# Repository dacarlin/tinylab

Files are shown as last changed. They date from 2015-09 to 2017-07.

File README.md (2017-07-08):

# TinyLab: Open Source Laboratory Robotics 

TinyLab is a collection of hardware design, protocols, and parts for building a modern biological laboratory using off-the-shelf parts and a 3D printer. Started as a [liquid handling kit for 3D printers](https://github.com/ryneches/tinylab), TinyLab is an open, collaborative project that seeks to provide researchers around the world the ability to create their own low cost, high quality tools for molecular biology, protein design, and organism design. 

## Contributing 

Contributions are welcome! This project is still in its early stages, and we welcome contributions at any level, from high-level approach advice to detailed plans and designs. Send us a pull request, or an email if we have help. Thanks! 

## Hardware 

### Block: Pipet Affector 

A open source design of a single-channel pipet affector module that can be built from off-the-shelf parts and 3D-printed designs provided here. 

#### Assembly 

1. 3D print the provided parts 
2. Purchase the items from the BOM 
3. Assemble according to instructions in `README.md` in `pipet` directory 

### Much4: Cartesian Frame Bot 

Open build from OpenBuilds.org ([Much4](http://www.openbuilds.com/threads/much4-a-printed-version-of-the-laser-v.547/)) showing a simple XY Cartesian bot that accepts our `pipet` design. 

### Jordan: Liquid Handler 

Second iteration (cantilever) liquid handling robot, nicknamed "Jordan". 

#### Assembly 

1. Print the parts in `parts/cantilever` and `parts/pipet`
1. Bolt the frame together 
1. Bolt on printed parts 
1. Install motors and electronics and test 
1. Run belts and pulleys 
1. Instal pipet assembly (see `pipet`) 

## Software 

### Autoprotocol-GCode Compiler 

Originally, this project was based on Transcriptic's [Autoprotocol language for specifying biological protocols](http://autoprotocol.org). However, since Transcriptic is no longer available for use, this may be of only historical interest. 

### WetTraffic: Liquid Handler Control 

Enables control of Jordan Liquid Handler using Python. 

### Trains: Scheduler 

Scheduler for handling the carriages that move plates between instruments in the work cell.

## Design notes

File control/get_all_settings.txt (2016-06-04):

{"1":n}    return motor 1 settings
{"2":n}
{"3":n}
{"4":n}
{"x":n}    return X axis settings
{"y":n}
{"z":n}
{"a":n}
{"b":n}
{"c":n}
{"sys":n}  return system settings
{"pos":n}  return work coordinate positions fox XYZABC axes. In mm or inches depending on G20/G21
{"mpo":n}  return absolute machine positions fox XYZABC axes. Always in mm, regardless of G20/G21
{"ofs":n}  return current offsets fox XYZABC axes. Sums coordinate system and G92 offsets. in mm.
{"hom":n}  return homing state fox XYZABC axes, and 'e' for the entire machine. 1=homed, 0=not.
{"p1":n}   return PWM channel 1 settings (currently there is only 1 PWM channel)
{"g54":n}  return offsets for work coordinate system #1 (G54)
{"g55":n}  #2
{"g56":n}  #3
{"g57":n}  #4
{"g58":n}  #5
{"g59":n}  #6
{"g92":n}  return G92 offsets currently in effect
{"g28":n}  return coordinate saved by G28 command
{"g30":n}  return coordinate saved by G30 command

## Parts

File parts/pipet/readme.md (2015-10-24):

# Liquid handler single-channel effector 

A free, open source (GNU license) liquid handling effector by Russell Neches and Alex Carlin 

## Materials

Item | Source | Part number | Note 
-----|--------|-------------|-------
stepper motor, NEMA 17 | Sparkfun | [10846](https://www.sparkfun.com/products/10846) | 400 steps per revolution
shaft coupler | Sparkfun | [12325](https://www.sparkfun.com/products/12325) | 
tuberculin syringes, 1 mL (without needle) | Fisher | | 
Delrin sheet, 1/8" thick | McMaster | | 100 mm x 200 mm is enough 
M3 machine screws, 60 mm long | McMaster | | 
Delrin hollow tube | McMaster | 8627K139 | 1' length is enough 
automotive fuel line | McMaster | | Any relatively stiff tube will work
home switch | Sparkfun | | 
lead screw, 1/16" travel per turn | McMaster | [99030a032](http://www.mcmaster.com/#99030a032/=w252r2) | 3' length is plenty 
travelling nut | McMaster | [95072a881](http://www.mcmaster.com/#95072a881/=w263xe) |
tap, 0.563"-18 | McMaster | | 

(parts list from Russell's email Wed, Feb 25, 2015)

## Assembly instructions 

1. Laser cut the `2d_moving_head.scad` and `2d_syringe_block.scad` models
2. Print the home switch mount 
1. Cut the Delrin tube to 54 mm 
4. Cut the lead screw to length 
5. Wire up the home switch and motor and test 
2. Dissassemble the syringes 
3. Mount the syringes in the syringe block. They should fit very firmly. Add a drop of epoxy if necessary 
4. Tap the moving head
5. Insert the syringes into the tapped head, and tighten down with the lead screw nut 
6. Thread the lead screw through the travelling nut, about halfway through  
7. Attach the coupler to the motor shaft
8. Mount the head by inserting the lead screw into the coupler and tightening the set screw 
9. Skewer the syringe block with the long M3 screws, and thread on the Delrin tube 
10. Cap the Delrin tubes with the home switch mount 
10. Insert the syringe pistons into the syringe bodies and the M3 machine screws into the motor
11. Make sure everything lines up 
12. Tighten the screws to finish up 

## How to use the effector 

The effector can be used as a standalone electronic pipet weilded by a human, as the primary effector 
in a liquid handling robot (see the `cantilever` design by Alex in this repository), and as a modification
to an existing 3D printer to enable the printer to be used as a liquid handling robot. 

### How to use the effector as an electronic pipet 

To use the effector as an electronic pipet, wire the stepper motor to a Raspberry Pi and use the 
included software (see `control` in this repository). You will need to wire up the buttons and LED 
display yourself. This is a work in progress and comments and pull requests are welcomed (GNU license)! 

### How to use the effector as a modification to a 3D printer 

To use the effector as a modifcation to a 3D printer, you have two options. If your printer has the 
necessary electronics to handle a second extruder, wire the stepper motor up as a second extruder, making
sure to disable temperature sensing. 

If your 3D printer has electronics only for a single extruder, you will have to replace the extruder 
with the liquid handling effector. 

You can use the Python packages in `control` to control your modified printer. Again, the software is a 
work in progress, and patches and pull requests are welcomed!

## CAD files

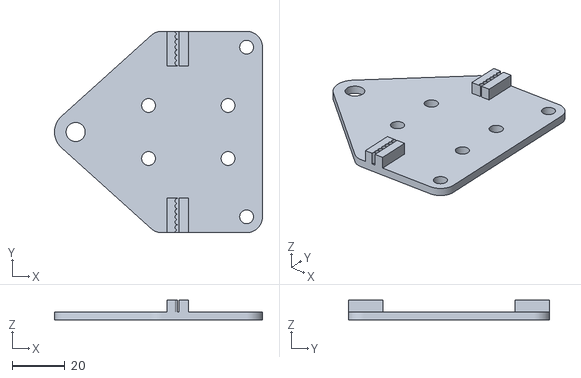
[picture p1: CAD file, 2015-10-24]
parts/cantilever/triangle_carriage.stl
78.5 x 76.0 x 7.50

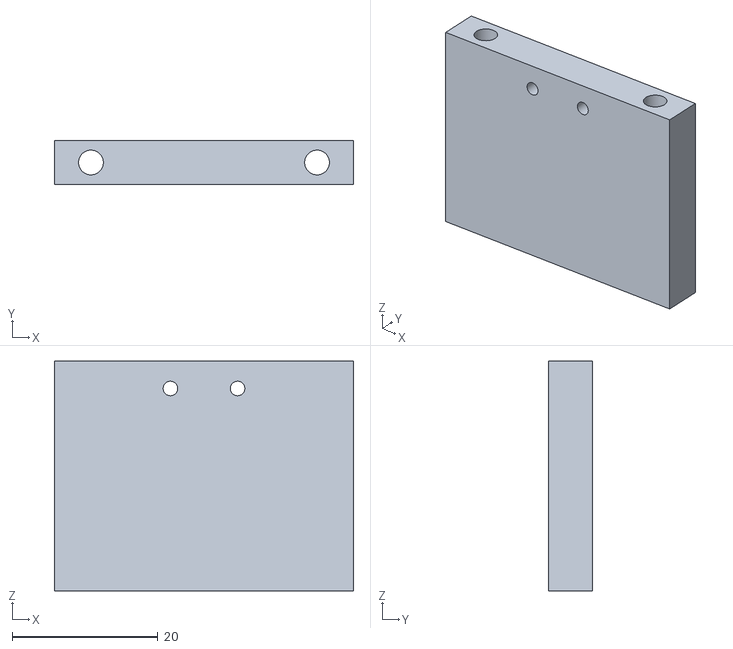
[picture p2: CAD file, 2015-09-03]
parts/pipet/home_switch_mount.stl
41.0 x 6.00 x 31.5

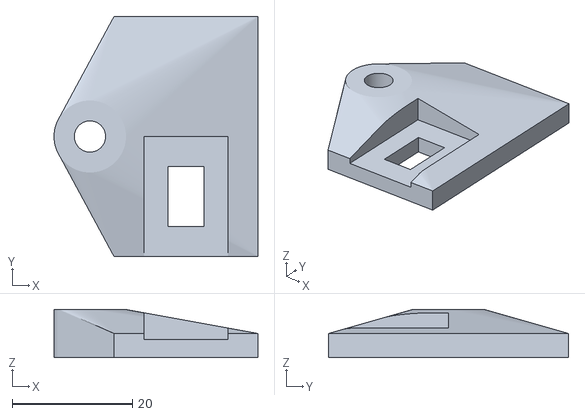
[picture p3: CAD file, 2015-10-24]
parts/cantilever/idler_mount.stl
34.0 x 40.0 x 8.00

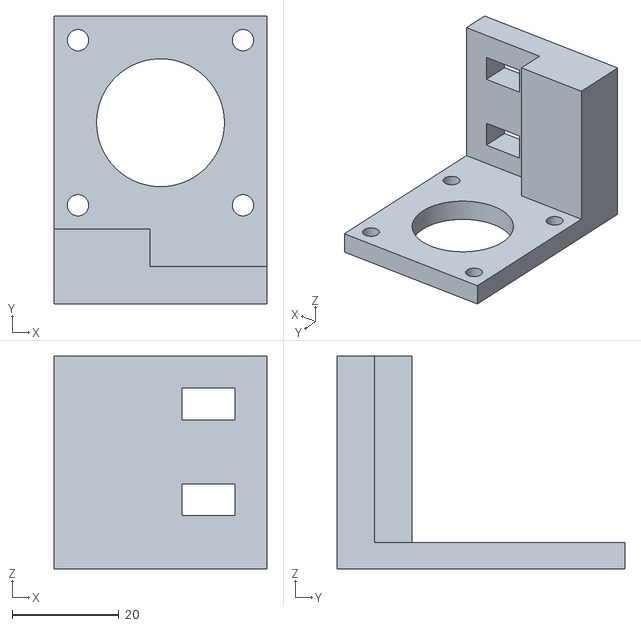
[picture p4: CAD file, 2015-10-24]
parts/cantilever/z_motor_mount.stl
40.0 x 54.0 x 40.0

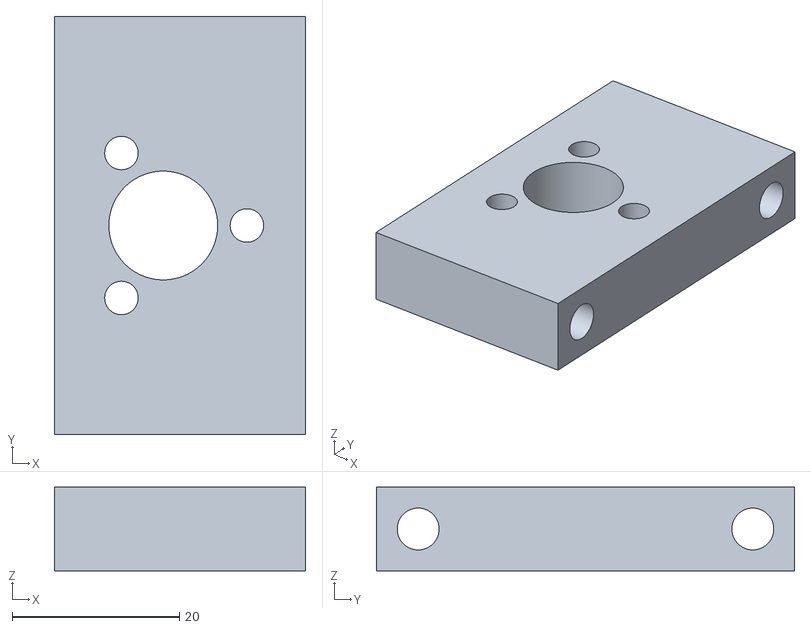
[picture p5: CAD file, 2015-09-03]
parts/cantilever/travelling_nut_mount.stl
30.0 x 50.0 x 10.0

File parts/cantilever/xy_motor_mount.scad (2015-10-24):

$fn=99; 

difference() {
    union() {
        cube([40,80,4]); // base
        translate([26,0,0]) cube([14,56,8]); // fin
    }
    
    // motor mount holes
    for(i=[0,1]) for(j=[0,1]) translate([4.5+31*i,4.5+31*j,0]) cylinder(r=2, h=30, center=true); 
    translate([20,20,0]) cylinder( r=12, h=30, center=true ); 
    
    // makerslide mount
    translate([4,50,-1]) cube([12,6,10]); 
    translate([4,68,-1]) cube([12,6,10]); 
    
    // home switch mount 
    translate([23.5,74,0]) cylinder( r=1, h=10, center=true ); 
    translate([32,74,0]) cylinder( r=1, h=10, center=true ); 
}

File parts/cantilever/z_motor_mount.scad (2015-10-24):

$fn=99; 

difference() {
    cube([40,40,5]); 
    for(i=[0,1]) for(j=[0,1]) translate([4.5+31*i,4.5+31*j,0]) cylinder(r=2, h=10, center=true); 
    translate([20,20,0]) cylinder( r=12, h=10, center=true ); 
    translate([4,50,-1]) cube([32,6,10]); 
    translate([4,68,-1]) cube([32,6,10]); 
    translate([4,50,-1]) cube([32,6,10]); 
}

rotate([90,0,0]) 
difference() {
    cube([40,40,14]); 
    translate([24,10,-1]) cube([10,6,30]); 
    translate([24,28,-1]) cube([10,6,30]); 
    translate([18,5,0]) cube([24,40,7]);
}

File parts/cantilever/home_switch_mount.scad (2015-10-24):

$fn=99; 

difference() {
  intersection() {
    cube([40,40,5], center=true); 
    rotate([0,0,45]) cube([40,40,5], center=true); 
    translate([0,10,0]) cube([40,40,5], center=true); 
  }
  cube([32,6,10], center=true); 
  for(i=[-1,1]) translate([4.75*i,12,0]) cylinder(r=1,h=10,center=true); 
      for(i=[-1,1]) translate([4.75*i,12,4]) cylinder(r=3,h=10,center=true); 
}

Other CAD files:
parts/cantilever/idler_mount.scad
parts/cantilever/pulley.scad
parts/cantilever/tip_holder.scad
parts/cantilever/travelling_nut_mount.scad
parts/cantilever/triangle_carriage.scad
parts/dispenser/8-tip.scad
parts/dispenser/idler.scad
parts/dispenser/lead_screw_hex.scad
parts/dispenser/y_mount.scad
parts/much4/tray_corner.scad
parts/pipet/2d_moving_head.scad
parts/pipet/2d_syringe_block.scad
parts/pipet/home_switch_mount.scad
parts/pipet/tip.scad
parts/single_channel_liquid_handler/head_plate.scad
parts/single_channel_liquid_handler/z_head.scad

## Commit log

2015-08-18 Fixes to parts
    [carriage.scad, motor-mount-sandbox.scad, motor_mount.scad, motor_mount.stl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]
2015-08-28 Designed a Y carriage
    [y_carriage.scad]
2015-09-03 Updating parts
    [2d_moving_head.dxf, 2d_moving_head.scad, 2d_syringe_block.dxf, 2d_syringe_block.scad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]
2015-09-03 Added triangle carriage
    [triangle_carriage.scad, triangle_carriage.stl]
2015-09-03 Slick updates to the carriage
    [triangle_carriage.scad]
2015-09-03 Updated XY motor mount with mounting holes for home switch
    [x_y_motor_mount.scad]
2015-09-06 Added instructions for assembly of the effector
2015-09-09 Cleaned up
    [2d_moving_head.dxf, 2d_syringe_block.dxf, carriage.scad, motor-mount-sandbox.scad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]
2015-09-15 Moved belt clip on triangle carriage
    [triangle_carriage.scad, triangle_carriage.stl]
2015-09-17 Added pipet tip
    [tip.scad]
2015-09-17 Still messing with the spacing of triangle carriage, think it is right now
    [triangle_carriage.scad, triangle_carriage.stl]
2015-09-17 Added slick idler mount
    [idler_mount.scad]
2015-09-17 Fixed home switch spacing in XY motor mount
    [xy_motor_mount.scad]
2015-09-17 Moved belt clips 1 mm away from center on triangle carriage
    [triangle_carriage.scad]
2015-09-17 Adjusted spacing on travelling nut mount and prettified
    [travelling_nut_mount.scad]
2015-09-17 Added a reversible home switch mount
    [home_switch_mount.scad]
2015-09-22 Added lame tip holder
    [tip_holder.scad]
2015-10-06 Added an improved pulley, fatter Z motor mount, and idler mount
    [idler_mount.stl, pulley.scad, z_motor_mount.scad, z_motor_mount.stl]
2015-10-15 Added a fin to the XY motor mount
    [xy_motor_mount.scad]
2015-10-24 Added 8-tip prototype
    [8-tip.scad]
2015-10-24 Some parts for dispenser
    [idler.scad, lead_screw_mount.scad]
2015-10-24 Added lead screw nut mount
    [lead_screw_hex.scad]
2015-10-24 Widened apertures
    [lead_screw_hex.scad]
2016-06-04 Added some things
    [lead_screw_hex.scad, lead_screw_mount.scad, y_mount.scad]
2016-06-13 Updates to interactive_control
    [tray_corner.scad]
2017-07-08 Reorganizing parts files
    [head_plate.scad, z_head.scad]
